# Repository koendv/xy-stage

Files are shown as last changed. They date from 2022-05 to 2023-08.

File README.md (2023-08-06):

# Microscope XY Stage

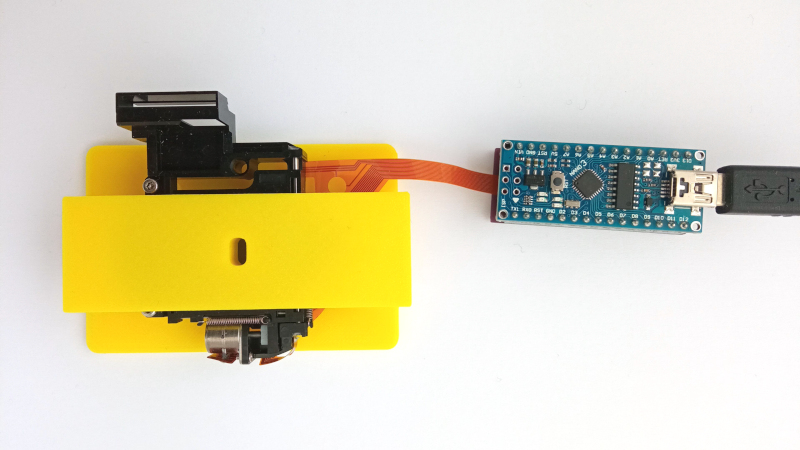
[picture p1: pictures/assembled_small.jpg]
assembled


This is a small computer-controlled mechanical microscope stage, with a movement of 2.4mm in both x and y, with a resolution of 5 &micro;m. Design goal is low component cost.

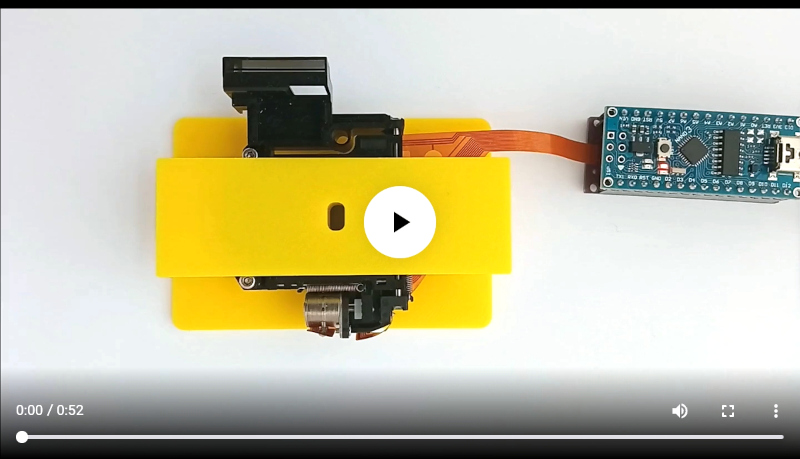
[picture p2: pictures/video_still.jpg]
video (https://vimeo.com/698148429)


[video](pictures/xy_stage.mp4) of the stage in motion.

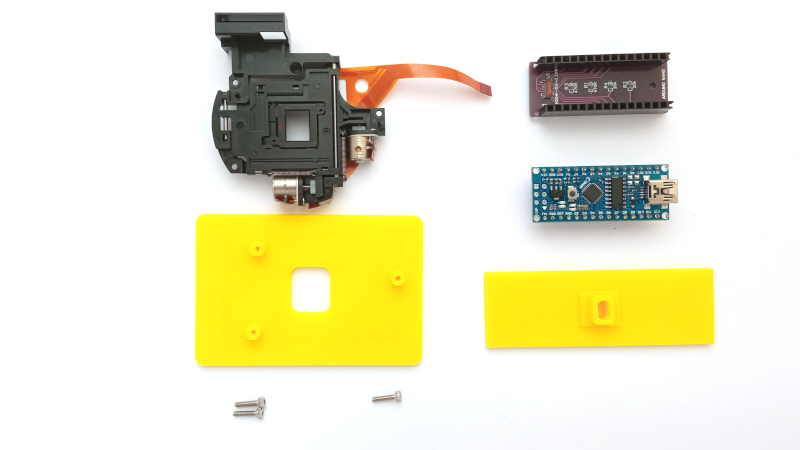
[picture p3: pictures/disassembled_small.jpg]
disassembled


The stage consists of

- mechanical part
- adapter plates
- connector board
- arduino nano controller
- firmware

## mechanical part

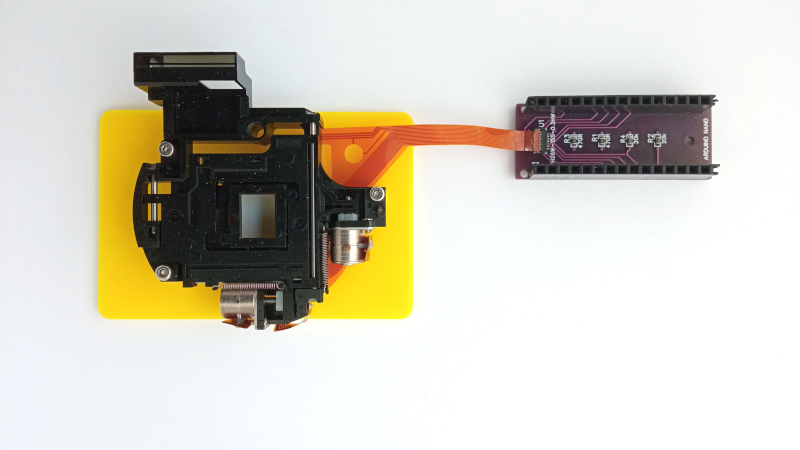
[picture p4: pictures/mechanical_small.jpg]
mechanical


Picture of mechanical part (to the left) and connector board (to the right).
The mechanical part is the [motion compensation part of a digital camera](https://www.aliexpress.com/item/32972295033.html), bought from aliexpress. All signals are on a flat flexible cable.

The mechanical part consists of a small carriage, two stepper motors and two slotted optocouplers, one for x and one for y. The stepper motors have a step size of  10 &micro;m. The stepper motors are run in half-stepping mode, resulting in a resolution of  5 &micro;m.

## adapter plates

The adapter plates give the microscope stage a flat base to sit on, and a flat top to put a microscope slide on.

The [adapter plates](openscad/) are designed in openscad and 3D printed. The size of the carriage is 25mmx75mm, the same as a standard microscope slide. I've snipped a few plastic pieces off from the movement to make everything fit. Holes can be threaded with hand tapping tools, or reamed with a small drill.

## connector board

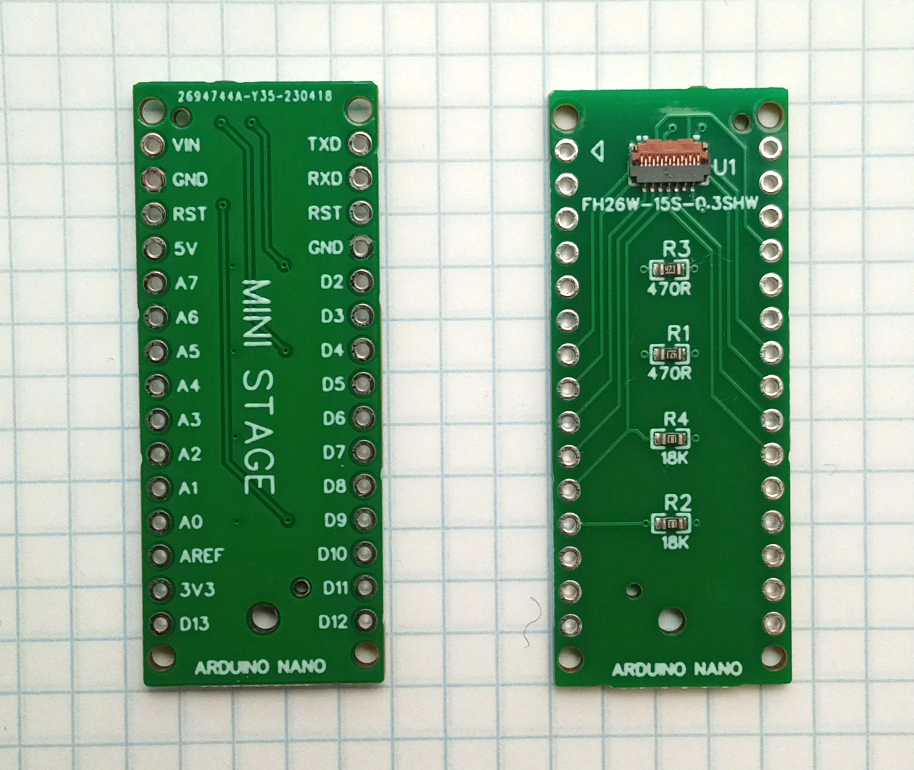
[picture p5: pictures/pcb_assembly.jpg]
pcb connector board


The [connector board](easyeda/Schematic_xy%20stage%20breakout_2023-05-13.pdf) breaks out the flat cable to the arduino pins. The xy stage contains two optical endstops, one for x and one for y. This is the [schematic](pictures/xystage_endstop.pdf) of one such optical endstop. There are current-limiting resistors for the optocoupler led, and pull-down resistors for the optocoupler output.  The stepper motors are so small you can connect them directly to the microcontroller pins.

The flat cable connector has a small tab. Lift the tab to insert or remove the flat cable. Push the tab down to fix the flat cable in place.

The [board project is at easyeda](https://oshwlab.com/koendv/xy-stage-breakout); and I've put up [gerbers at github](easyeda/).

The easiest way to obtain a pcb board is to have it assembled for you. All files needed for pcb assembly are in the [easyeda](easyeda/) directory:

- Gerber files
- Bill of Materials ("BOM")
- Pick and Place file ("CPL")

The Gerber files order the printed circuit board. The Bill of Materials orders the components. The Pick and Place file orders the components to be soldered to the board.

This is a walk-through of the ordering process:

- Log in to [jlcpcb.com](https://jlcpcb.com/).
- Click "Order now"
- Click "Add gerber file"
- Select file "Gerber_PCB_xy stage breakout_2023-05-13.zip"
- Select "PCB Assemly"
- Choose "Assemble top side"
- Click "Confirm"
- Click "Next"
- Click "Add BOM File"
- Select file "BOM_PCB_xy stage breakout_2023-05-13.csv"
- Click "Add CPL File"
- Select file "PickAndPlace_PCB_xy stage breakout_2023-05-13.csv"
- Click "Process BOM and CPL"
- Next to the flat cable connector it says "No part selected". Click "Search". After the part has been found, click "Select".
- Click "Next"
- In product description, choose "Research/Education/DIY/Entertainment", "DIY"
- Click "Save to cart"
- Check out order

Make sure all parts are available before ordering assembly.

## arduino nano controller

The microcontroller is a 5V 16MHz arduino nano. This processor was chosen because it can drive the stepper motor pins directly, at low cost. The arduino nano plugs in in the connector board.

Two firmware are available for the xy stage: an arduino sketch and the grbl g-code motion controller.

## arduino sketch

The [arduino/ directory](arduino/) contains an arduino project for the xy stage.
To install this firmware in the arduino nano, start up the arduino IDE. Open the file [xystage.ino](arduino/xystage/xystage.ino) in the arduino IDE,
In the arduino IDE, choose "Tools -> Board -> Arduino AVR Boards -> Arduino Nano", compile and upload.

Connect to the arduino serial port with a terminal emulator, and get this prompt:

```
xy stage - w forward s backward a left d right x home
ok
```

Move the stage using the WASD keys: w is forward, s is backward, a is left, d is right. x homes the stage, and if you press shift the stage moves ten times faster.

| key | action |
|---|---|
| w | forward 1 step |
| s | backward 1 step |
| a | left 1 step |
| d | right 1 step |
| W | forward 10 steps |
| S | backward 10 steps |
| A | left 10 steps |
| D | right 10 steps |
| x | home |

If after power-up the led blinks and the serial console prints  ``error`` then homing failed. Check the flat flexible cable connections, and that the carriage can move freely.

## grbl

grbl logo (https://github.com/gnea/grbl/wiki)

[grbl](https://github.com/gnea/grbl/wiki) is a g-code motion controller for the arduino nano. grbl allows stage control using G-code commands.

Example: Set the feed rate. Starting at the origin, first move the stage 1 mm in x, then 1 mm in y.

```
> Grbl 1.1h ['$' for help]
< F100
> ok
< G1X1
> ok
< G1Y1
> ok
```

See the [grbl/ directory](grbl/) for grbl firmware for the arduino nano.

Using G-code is interesting if you wish to automate a microscope.

## micro-manager

[micro-manager](https://micro-manager.org/) is open source software for control and automation of microscope hardware. See the [micro-manager/ directory](micro-manager/) for using the xy-stage with micro-manager.

## closing thoughts

Looking back, the adapter plates could easily be improved. The adapter plates were printed in yellow, on a Prusa FDM printer. If I had to do this again, I would 3D print the adapter plates in a matte dark grey or black, not yellow. Using SLS or MJF, not FDM, to be able to design a carriage that weighs less yet is more rigid. And probably ordered at [jlcpcb](https://3d.jlcpcb.com/), the same place I had the printed circuits made.

## bill of Materials

The list of materials used to build this project:

|Name|Part|Qty|
|---|---|---|
|R1, R3|470R 0603|2|
|R2, R4|18K 0603|2|
|U1|Hirose FH26W-15S-0.3SHW(60)|1|
||20pin 2.54mm single row female header|2|
||arduino nano 3.0 atmega328|1|
||[small xy stage](https://www.aliexpress.com/item/32972295033.html)|1|
||M2x8 screw|3|
||pcb|1|
||3D printed parts|1|

ko-fi (https://ko-fi.com/Q5Q03LPDQ)

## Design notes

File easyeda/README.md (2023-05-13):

These are the design files for the connector board.
The connector board is a [project at easyeda](https://oshwlab.com/koendv/xy-stage-breakout).

- [Schematic](Schematic_xy stage breakout_2023-05-13.pdf)
- [PCB](PCB_PCB_xy stage breakout_2023-05-13.pdf)
- [Gerbers](Gerber_PCB_xy stage breakout_2023-05-13.zip).
- [Bill of Materials](BOM_PCB_xy stage breakout_2023-05-13.csv)
- [Pick and Place file](PickAndPlace_PCB_xy stage breakout_2023-05-13.csv)

The Gerbers order the printed circuit board; the Bill of Materials orders the components, and the Pick and Place file orders the components to be soldered to the printed circuit board.

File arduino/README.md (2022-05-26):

## Arduino project
This is the arduino project for the xy stage. Open the file "xystage.ino" in the Arduino IDE,
In the arduino IDE, choose "Tools -> Board -> Arduino AVR Boards -> Arduino Nano", compile and upload.

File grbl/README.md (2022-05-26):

# grbl for h-bridge

grbl is controller software that allows stage control using G-code commands.

This directory contains a patch to use the [grbl](https://github.com/gnea/grbl) G-code controller with the xy microscope stage.  This patch is needed because

- the steppers are connected to the controller pins as h-bridge, while grbl expects step/direction stepper drivers.
- the xy stage has homing switches at the center of the stage, while grbl prefers limit switches at the end of the stage.

## compilation

The flash upload command may differ for your setup. For compilation on linux, install arduino ide and set the path to use avr-gcc and avrdude from arduino:

```
export PATH=~/.arduino15/packages/arduino/tools/avr-gcc/7.3.0-atmel3.6.1-arduino7/bin/:~/.arduino15/packages/arduino/tools/avrdude/6.3.0-arduino17/bin/:$PATH
git clone https://github.com/koendv/xy-stage
git clone https://github.com/gnea/grbl
cd grbl/
patch -p1 < ../xy-stage/grbl/grbl_1_1h.patch
make
make flash
```

For compiling on Windows using the Arduino IDE, see [compiling GRBL](https://github.com/gnea/grbl/wiki/Compiling-Grbl)

## links

- [GRBL-H-Bridge](https://github.com/rakshithbk/GRBL-H-Bridge)
- [h-grbl](http://xn--zabaaganionemiejsce-8fd.pl/arduino/h-grbl/)

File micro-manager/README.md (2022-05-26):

# micro-manager

[micro-manager](https://micro-manager.org/) is open source software for control and automation of microscope hardware. This is a micro-manager driver for a mechanical stage that uses a grbl controller.

Instead of writing a separate driver for grbl, this patches the existing micro-manager RAMPS driver to use grbl g-code.

## compile

Patch micro-manager sources with _micro-manager-grbl.patch_:
```
 $ git clone --recursive https://github.com/micro-manager/micro-manager/
 $ cd micro-manager/mmCoreAndDevices/
 $ wget https://raw.githubusercontent.com/koendv/xy-stage/main/micro-manager/micro-manager-grbl.patch
 $ patch -p1 < micro-manager-grbl.patch
patching file DeviceAdapters/CNCMicroscope/RAMPSStage/RAMPS.cpp
patching file DeviceAdapters/CNCMicroscope/RAMPSStage/RAMPS.h
```

[Compile and install](https://github.com/micro-manager/micro-manager/blob/main/doc/how-to-build.md).

## configure

To configure, choose Devices -> Hardware Configuration Wizard.

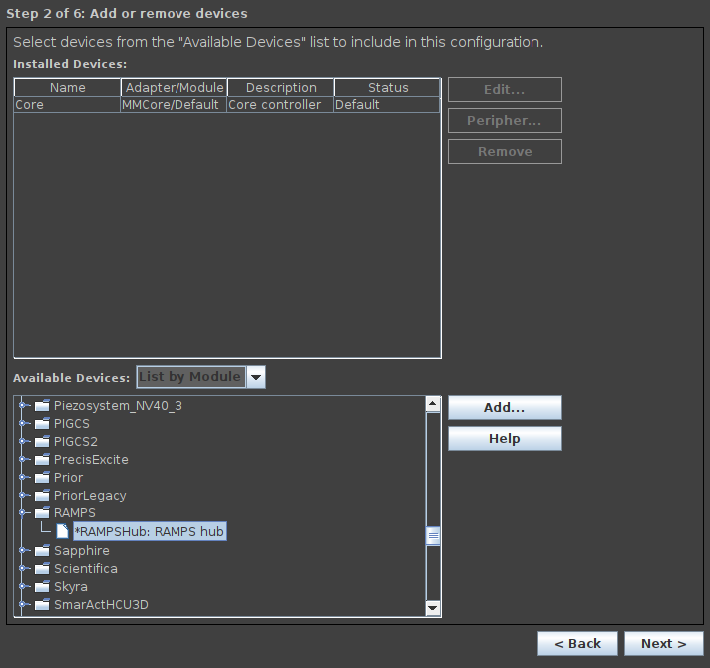
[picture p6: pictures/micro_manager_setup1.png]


Select xy stage serial port.

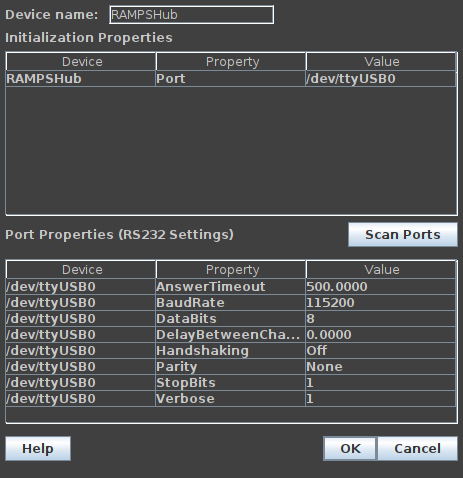
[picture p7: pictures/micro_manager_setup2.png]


Select only xy stage, not z stage.

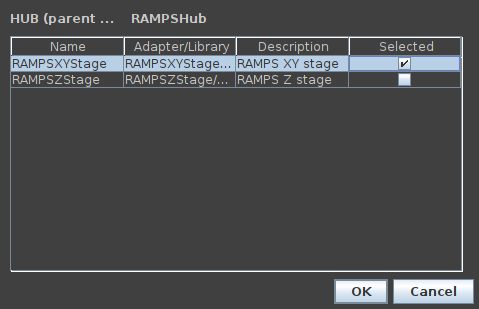
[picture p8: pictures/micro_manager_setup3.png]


Choose Devices -> Device Property Browser to set xy stage speed and acceleration. The values for RAMPSHub-Acceleration are written to grbl registers 120, 121 and 122. The values for RAMPSHub-Velocity are written to grbl registers 110, 111 and 112.

not truncated

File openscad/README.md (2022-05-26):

## openscad

disassembled.jpg

These are the design files for the adapter plates. The adapter plates are designed using [openscad](http://openscad.org). There are two versions of the carriage, one with a hole for illumination from below and one without.

- [source file](stage.scad)
- [stage top, solid](stage1.stl)
- [stage top, with hole for illumination](stage2.stl)
- [stage bottom](stageplate.stl)
- [stage bottom, with bracket to attach arduino nano](stageplate_arduinonano.stl)
- [stage floorplan](stage.svg)

Two 3D printing methods have been used:

- FDM, PETG material, [Prusa i3](https://www.treatstock.com/c/seaside-3d).
- SLA, LEDO 6060 resin, [jlcpcb 3d](https://jlcpcb.com/3d-printing)

In the end, how to print depends upon price.

Some ideas for improvements:

- more stable carriage, larger hole for through illumination if the other side of the xy table is up
- smaller and lighter carriage if 18x18x1mm cover slips are used instead of 75x25mm slides.
- arduino nano holder

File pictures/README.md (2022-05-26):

# pictures

|sliding table|
|---|
|assembled.jpg|
|mechanical.jpg|
|disassembled.jpg|
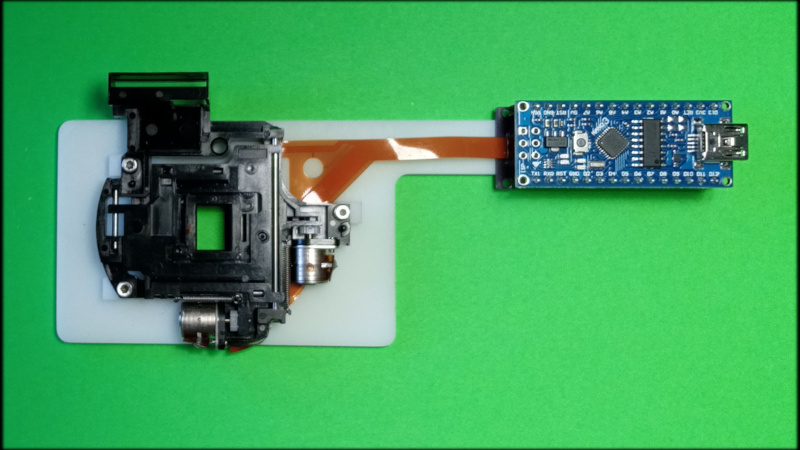
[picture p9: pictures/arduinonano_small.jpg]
arduinonano.jpg
||
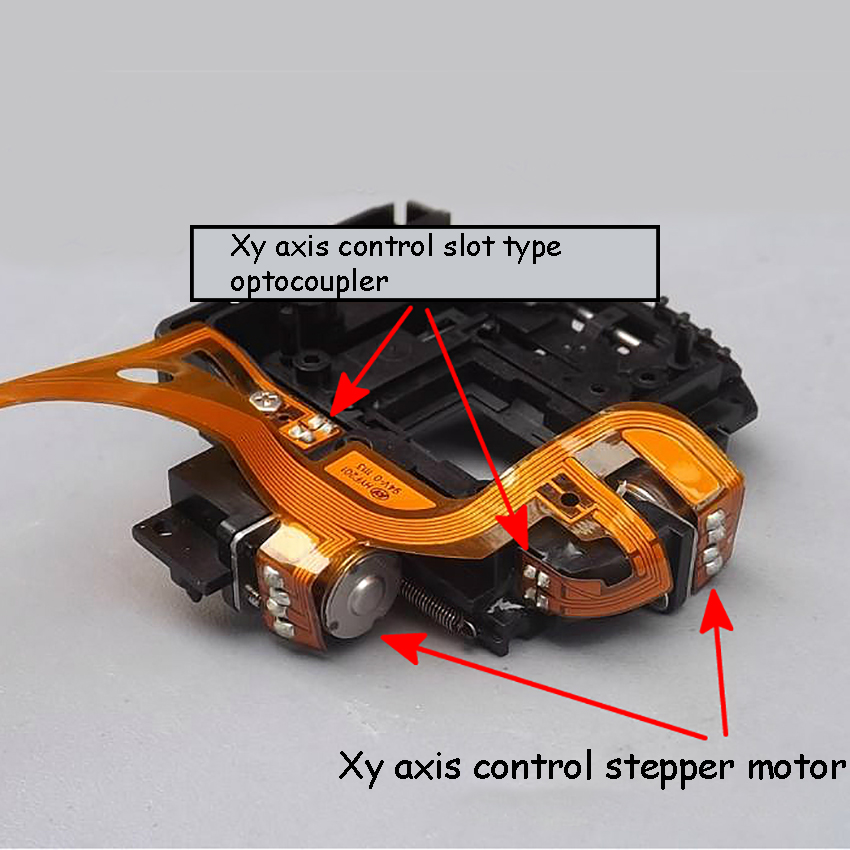
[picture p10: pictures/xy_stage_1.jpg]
xy_stage_1.jpg
||
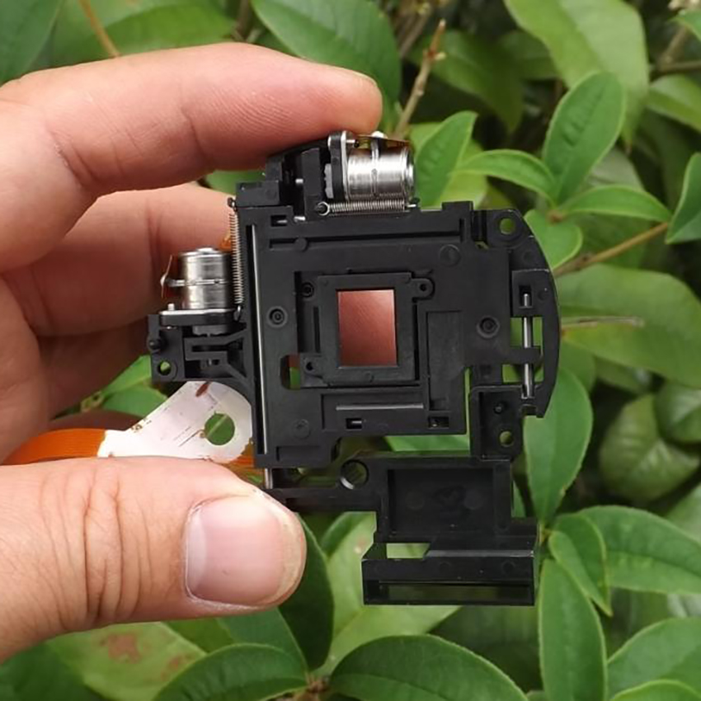
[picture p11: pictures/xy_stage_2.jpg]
xy_stage_2.jpg
||
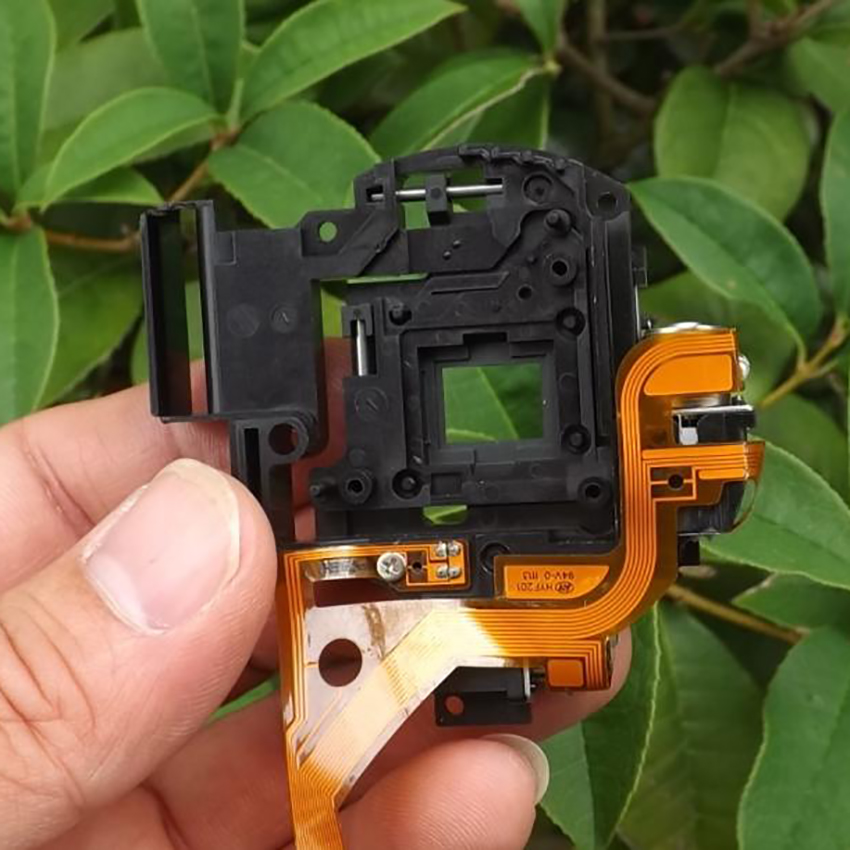
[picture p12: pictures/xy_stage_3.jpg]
xy_stage_3.jpg
||
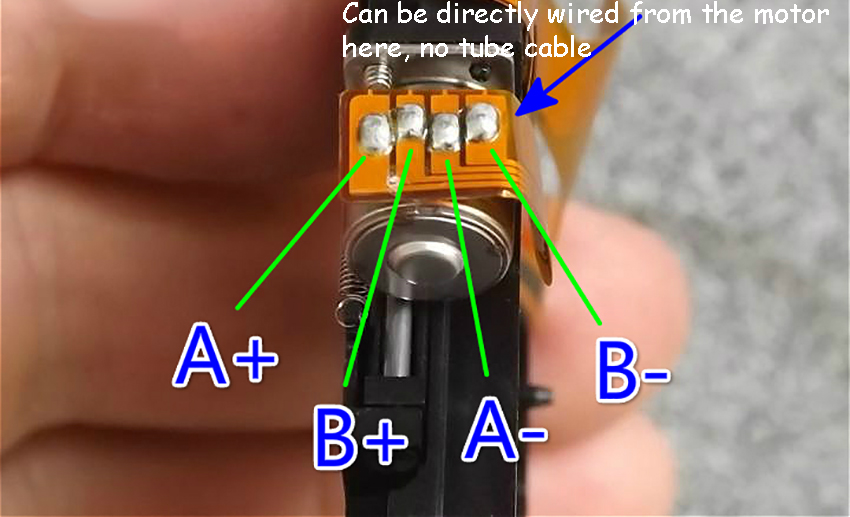
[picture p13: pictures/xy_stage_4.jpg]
xy_stage_4.jpg
||
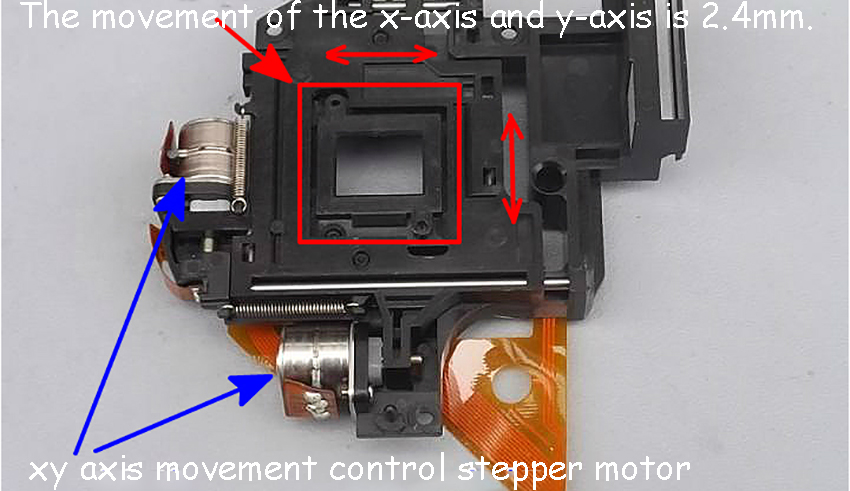
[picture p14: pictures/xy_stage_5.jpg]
xy_stage_5.jpg
||
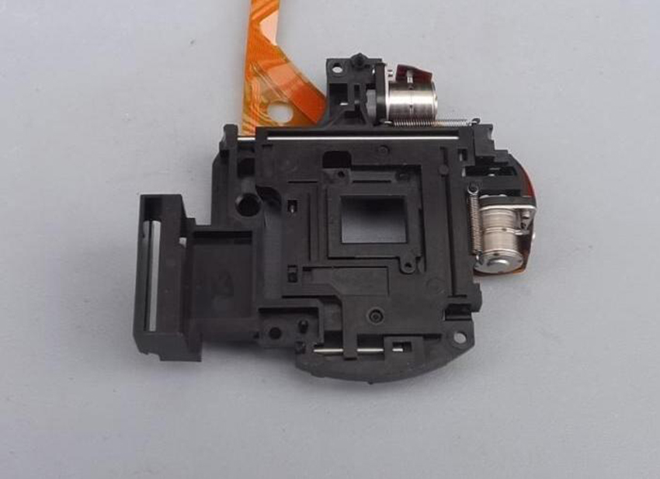
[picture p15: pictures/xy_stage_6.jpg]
xy_stage_6.jpg
||
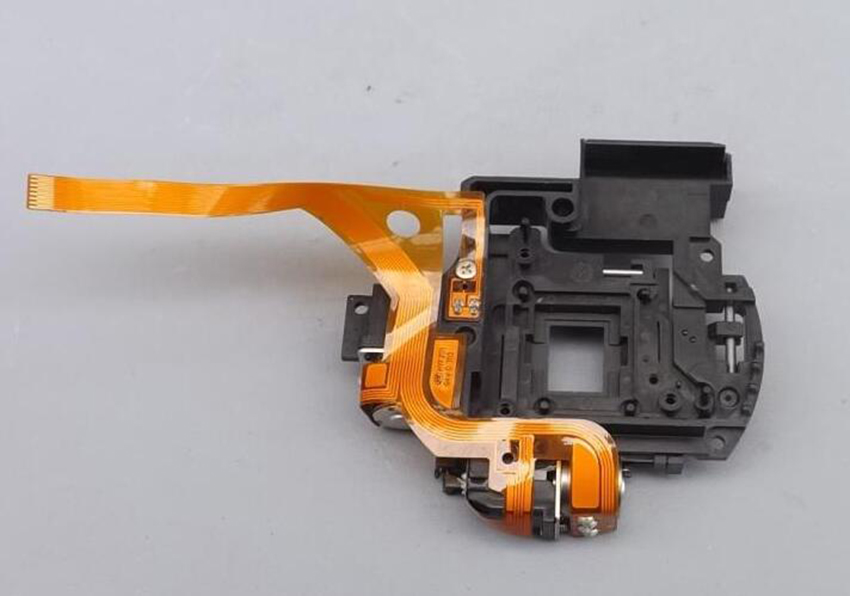
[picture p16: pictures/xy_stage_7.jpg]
xy_stage_7.jpg
||
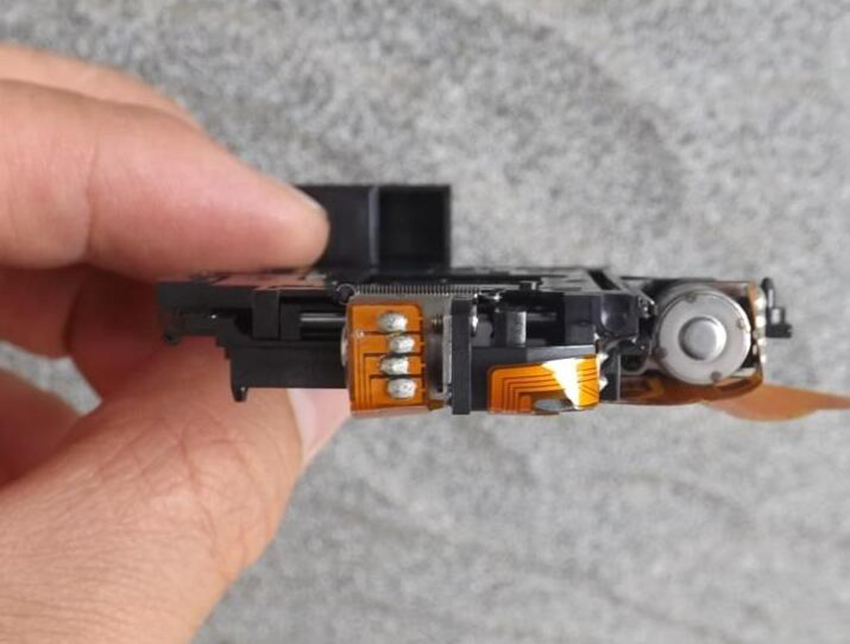
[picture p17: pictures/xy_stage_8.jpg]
xy_stage_8.jpg
||

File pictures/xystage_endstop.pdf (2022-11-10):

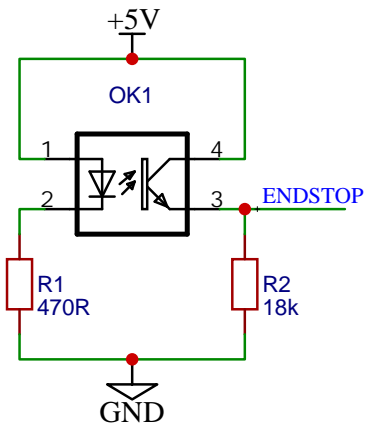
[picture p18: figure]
GND; ENDSTOP

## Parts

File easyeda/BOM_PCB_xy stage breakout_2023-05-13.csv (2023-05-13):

ID | Name | Designator | Footprint | Quantity | Manufacturer Part | Manufacturer | Supplier | Supplier Part | Price
1 | FH26W-15S-0.3SHW | U1 | FH26W-15S-0.3HW | 1 | FH26W-15S-0.3HW | Hirose | LCSC | C2840191
2 | 470R | R1,R3 | R0603 | 2 | 0603WAF4700T5E | UniOhm | LCSC | C23179 | 0.001
3 | 18K | R2,R4 | R0603 | 2 | 0603WAF1802T5E | UniOhm | LCSC | C25810 | 0.001
4 | HDR-F-2.54_1x15 | H1,H2 | HDR-F-2.54_1X15 | 2 |  |  | LCSC | C124408 | 0.204

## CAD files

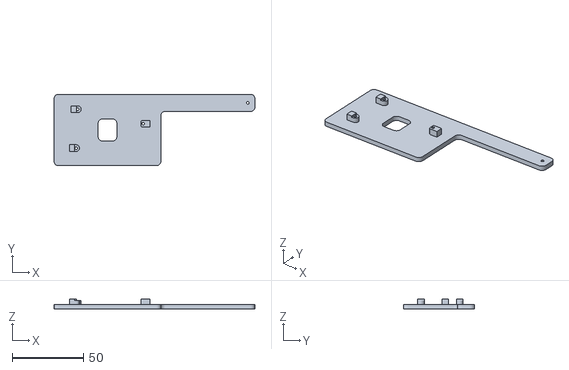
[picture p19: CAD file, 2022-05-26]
openscad/stageplate_arduinonano.stl
141.0 x 50.0 x 7.00

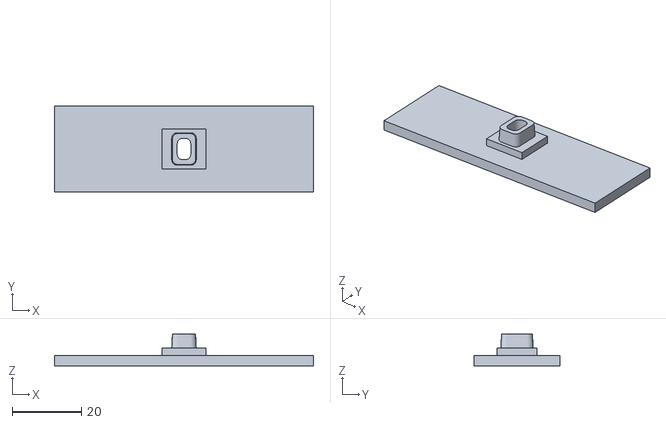
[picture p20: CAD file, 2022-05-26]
openscad/stage2.stl
75.0 x 25.0 x 9.20

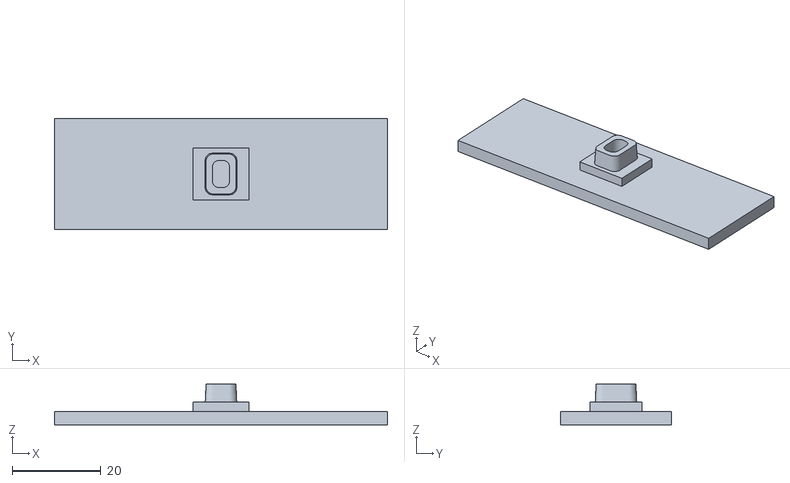
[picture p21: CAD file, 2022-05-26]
openscad/stage1.stl
75.0 x 25.0 x 9.20

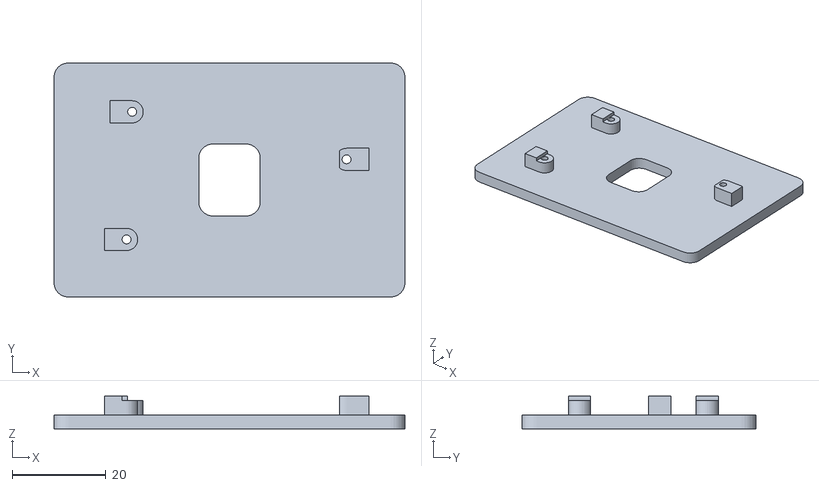
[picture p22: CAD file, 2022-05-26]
openscad/stageplate.stl
75.0 x 50.0 x 7.00

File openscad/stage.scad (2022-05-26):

$fn = $preview?16:32;
eps1 = 0.001;
eps2 = 2*eps1;
nozzle = 0.4;

plate_x = 75.0;
plate_y = 50.0;

// pillars for screws
d1 = 1.9;  // inner diameter pillar
d2 = 4.75; // outer diameter pillar
// screws
dscrew = 25.4;
alpha1 = 90+120;
alpha2 = 90+55;
alpha3 = 90-80;
// screw 1
x1 = dscrew * cos(alpha1);
y1 = dscrew * sin(alpha1);
t1 = (d2-d1)/2; // bump on pillar
cut1 = 0.9;     // bump on pillar
// screw 2
x2 = dscrew * cos(alpha2);
y2 = dscrew * sin(alpha2);
t2 = (d2-d1)/2; // bump on pillar
cut2 = 0.9;     // bump on pillar
// screw 3
x3 = dscrew * cos(alpha3);
y3 = dscrew * sin(alpha3);
t3 = -d2+0.9;   // cut on pillar
cut3 = 4.0;     // cut on pillar

// central hole size
l1 = 7.12;
l2 = 9.37;

h1 = 3.0;
h2 = 4.0;

dmax = 3.0;

// support for attaching arduino nano
pcb_support = true;

pcb_x = 66.0;
pcb_y = 12.0;
pcbscrew_x = pcb_x - 5.0;
pcbscrew_d = 2.0;

module stageplate() {
    difference() {
        stageplate_body();
        stageplate_holes();
    }
}

module stageplate_body() {
    translate([-plate_x/2, -plate_y/2, 0])
    linear_extrude(h1)
    offset(-dmax)
    offset(2*dmax)
    offset(-dmax)
    union() {
        square([plate_x, plate_y]);
        if (pcb_support)
        translate([plate_x, plate_y-pcb_y, 0])
        square([pcb_x, pcb_y]);
    }

    // screws
    translate([x1, y1, h1-eps1])
    difference() {
        union() {
            cylinder(h=h2, d=d2);
            translate([-d2, -d2/2, 0])
            cube([d2, d2, h2]);
        }
        translate([t1-d2/2, -d2, h2-cut1])
        cube([d2, 2*d2, h2]);
    }
    translate([x2, y2, h1-eps1])
    difference() {
        union() {
            cylinder(h=h2, d=d2);
            translate([-d2, -d2/2, 0])
            cube([d2, d2, h2]);
        }
        translate([t2-d2/2, -d2, h2-cut2])
        cube([d2, 2*d2, h2]);
    }
    translate([x3, y3, h1-eps1])
    difference() {
        union() {
            cylinder(h=h2, d=d2);
            translate([0, -d2/2, 0])
            cube([d2, d2, h2]);
        }
        translate([t3-d2/2, -d2/2, h2-cut3])
        cube([d2, d2, h2+eps1]);
    }
}

module stageplate_holes() {
    h = h1+h2+eps2;
    translate([x1, y1, -eps1])
    cylinder(h=h, d=d1);
    translate([x2, y2, -eps1])
    cylinder(h=h, d=d1);
    translate([x3, y3, -eps1])
    cylinder(h=h, d=d1);
    translate([-l1/2, -l2/2, -eps1])
    linear_extrude(h)
    offset(dmax)
    square([l1, l2]);
    // pcb
    if (pcb_support)
    translate([plate_x/2 + pcbscrew_x, plate_y/2-pcb_y/2, -eps1])
    cylinder(h=h, d=d1);
}


stage_x = 75.0;
stage_y = 25.0;
stage_z = 3.0;
foot_x = 13.0 - nozzle;
foot_y = 12.0 - nozzle;
foot_z = 2.2;
chamfer = 1.6;
wall_thickness = 1.6;
module stage(no_hole) {
    difference() {
        stage_body();
        stage_holes(no_hole); // no_hole = true or false
    }
}

module stage_body() {
    translate([-stage_x/2, -stage_y/2, 0])
    cube([stage_x, stage_y, stage_z]);
    translate([-foot_x/2, -foot_y/2, stage_z-eps1])
    cube([foot_x, foot_y, foot_z]);

    hull() {
        translate([0, 0, h1+foot_z+4])
        linear_extrude(eps1)
        offset(chamfer)
        offset(-chamfer)
        square([l1-nozzle, l2-nozzle], center = true);
        translate([0, 0, h1+foot_z])
        linear_extrude(eps1)
        offset(chamfer)
        offset(-chamfer)
        square([l1, l2], center = true);
    }
}

module stage_holes(solid = true) {
    translate([0, 0, solid ? -h1-foot_z-eps1 : 0])
    translate([-l1/2, -l2/2, h1+foot_z-eps1])
    linear_extrude(h1*10)
    offset(wall_thickness)
    offset(-2*wall_thickness)
    square([l1, l2]);
}

module assembly() {
    stageplate();
    translate([0, 0, 10])
    mirror([0,0,1])
    stage(false); // no hole in stage
}

assembly();
//projection()
//stageplate();
//stage(false); // no hole in stage
//stage(true); // hole in stage

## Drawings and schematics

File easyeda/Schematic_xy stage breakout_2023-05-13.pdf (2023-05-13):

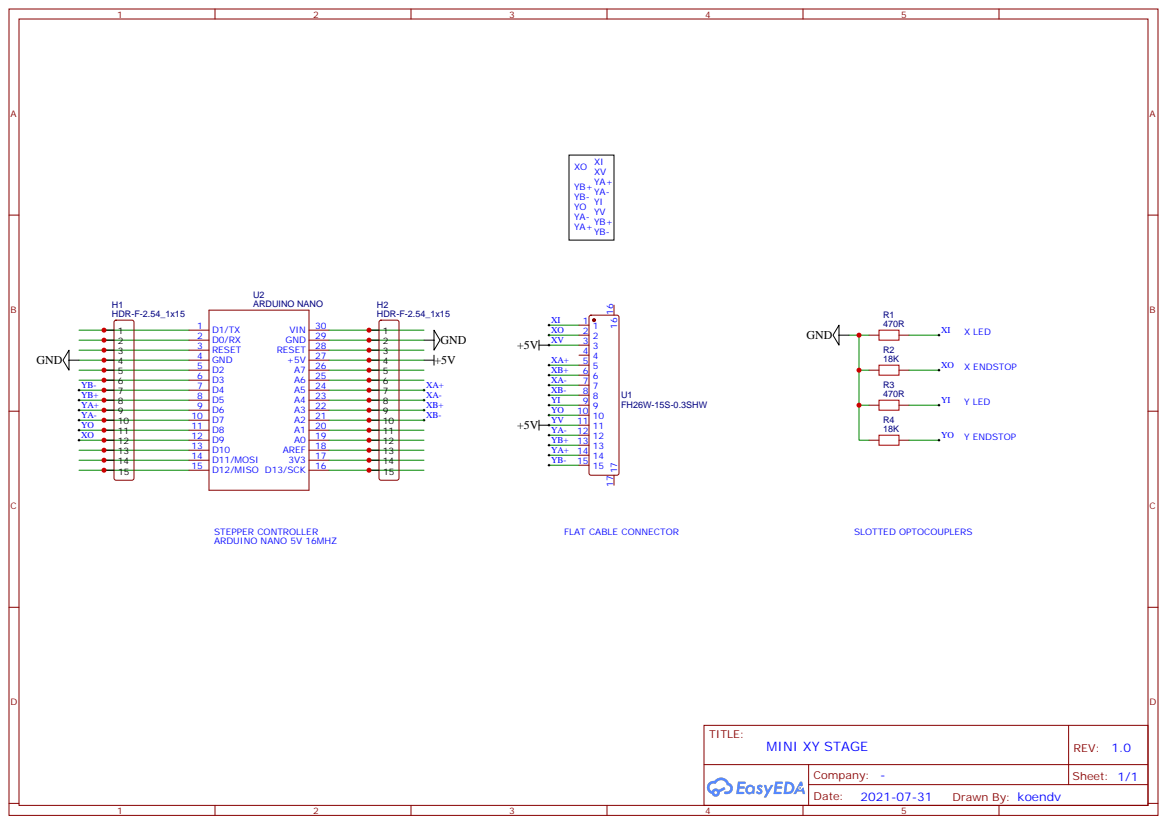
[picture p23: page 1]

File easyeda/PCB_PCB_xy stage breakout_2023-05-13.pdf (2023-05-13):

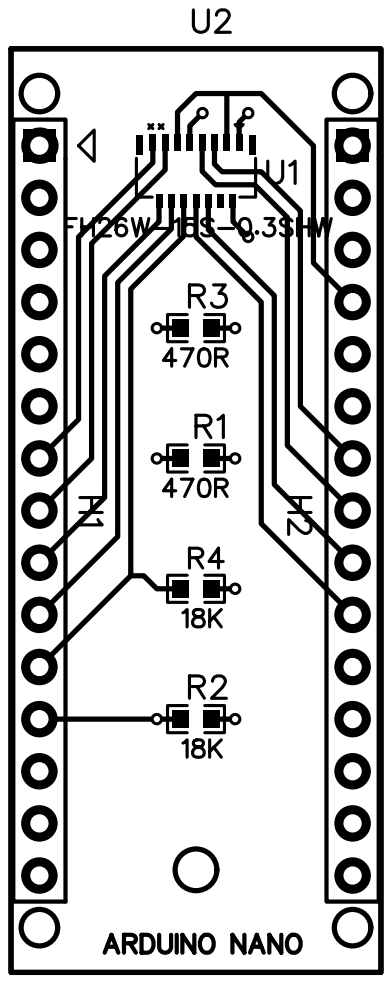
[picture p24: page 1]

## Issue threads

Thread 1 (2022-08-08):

### ISSUE TITLE
Connector board

### ISSUE THREAD

**Issue by gtnz** [koendv/xy-stage#1]
Hello. 
Sorry, I don’t know where on github they ask questions, so I open issue.

Where can I get a connector board like in your project?

**Comment by koendv** [comment]
Thank you for your interest. This is a good question.

The board I use I soldered myself, by hand. If you wish to, I can send it to you for 15 EUR + what the post office charges me to send a small packet.

Soldering by hand becomes unpractical, even for small numbers. There are companies like jlcpcb, seeedstudio, elecrow that do pcb assembly for you, but then you have not one board, but 5.

**Comment by koendv** [comment]
I added documentation how I ordered the pcb and components, see https://github.com/koendv/xy-stage#connector-board
HTH

**Comment by gtnz** [comment]
Thank you very much

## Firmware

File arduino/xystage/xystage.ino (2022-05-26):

/* 
 * microscope mechanical stage
 * commands:
 * w forward s backward a left d right q home
 * W fast forward S fast backward A fast left D fast right
 */

#include <Arduino.h>

// B (pin D8, D9: endstops)
// C (pin A2..A5: x stepper)
// D (pin D4..D7: y stepper)

// stop homing if homing switch does not change after HOME_MAX_STEPS steps
#define HOME_MAX_STEPS 720

#define X0_MAX 240
#define X0_MIN -240
#define Y0_MAX 240
#define Y0_MIN -240

#define ENDSTOP_X 8
#define ENDSTOP_Y 9

#define STEPPER_X_A1 (0x01 << PINC5)
#define STEPPER_X_A2 (0x01 << PINC4)
#define STEPPER_X_B1 (0x01 << PINC3)
#define STEPPER_X_B2 (0x01 << PINC2)

#define STEPPER_Y_A1 (0x01 << PIND4)
#define STEPPER_Y_A2 (0x01 << PIND5)
#define STEPPER_Y_B1 (0x01 << PIND6)
#define STEPPER_Y_B2 (0x01 << PIND7)

#define STEPPER_PORT_X PORTC
#define STEPPER_PORT_Y PORTD

#define STEPPER_DDR_X DDRC
#define STEPPER_DDR_Y DDRD

#define ALL_STEPPER_PINS_X (STEPPER_X_A1 | STEPPER_X_A2 | STEPPER_X_B1 | STEPPER_X_B2)
#define ALL_STEPPER_PINS_Y (STEPPER_Y_A1 | STEPPER_Y_A2 | STEPPER_Y_B1 | STEPPER_Y_B2)

const int stepper_table_x[8]{ STEPPER_X_A1, STEPPER_X_A1 | STEPPER_X_B1, STEPPER_X_B1, STEPPER_X_B1 | STEPPER_X_A2, STEPPER_X_A2, STEPPER_X_A2 | STEPPER_X_B2, STEPPER_X_B2, STEPPER_X_B2 | STEPPER_X_A1 };
const int stepper_table_y[8]{ STEPPER_Y_A1, STEPPER_Y_A1 | STEPPER_Y_B1, STEPPER_Y_B1, STEPPER_Y_B1 | STEPPER_Y_A2, STEPPER_Y_A2, STEPPER_Y_A2 | STEPPER_Y_B2, STEPPER_Y_B2, STEPPER_Y_B2 | STEPPER_Y_A1 };

static unsigned int step_x = 0;
static unsigned int step_y = 0;

static int x0 = 0;
static int y0 = 0;

bool homed = false;
uint32_t last_update_millis = 0;

void update_pins() {
  step_x %= 8;
  step_y %= 8;
  STEPPER_PORT_X = (STEPPER_PORT_X & ~ALL_STEPPER_PINS_X) | stepper_table_x[step_x];
  STEPPER_PORT_Y = (STEPPER_PORT_Y & ~ALL_STEPPER_PINS_Y) | stepper_table_y[step_y];
  delay(5);  // lower for faster
  last_update_millis = millis();
}

void idle_pins() {
  uint32_t now_millis = millis();
  if (now_millis > last_update_millis + 30000) {
    // sleep
    STEPPER_PORT_X = (STEPPER_PORT_X & ~ALL_STEPPER_PINS_X);
    STEPPER_PORT_Y = (STEPPER_PORT_Y & ~ALL_STEPPER_PINS_Y);
    last_update_millis = millis();
  }
}
void home() {
  int maxcnt;
  homed = false;
  maxcnt = HOME_MAX_STEPS;
  /* x axis  home */
  while (digitalRead(ENDSTOP_X)) {
    if (--maxcnt == 0) return;
    step_x += 7;
    update_pins();
  };
  while (!digitalRead(ENDSTOP_X)) {
    if (--maxcnt == 0) return;
    step_x += 1;
    update_pins();
  };
  /* y axis  home */
  maxcnt = HOME_MAX_STEPS;
  while (digitalRead(ENDSTOP_Y)) {
    if (--maxcnt == 0) return;
    step_y += 7;
    update_pins();
  };
  while (!digitalRead(ENDSTOP_Y)) {
    if (--maxcnt == 0) return;
    step_y += 1;
    update_pins();
  };
  x0 = 0;
  y0 = 0;
  homed = true;
}

// print coordinates in micron
void print_coords() {
  Serial.print(x0 * 5);
  Serial.print(' ');
  Serial.print(y0 * 5);
  Serial.println();
}

void stage_left() {
  if (x0 > X0_MIN) {
    step_x += 7;
    --x0;
    update_pins();
  }
}

void stage_right() {
  if (x0 < X0_MAX) {
    step_x += 1;
    x0++;
    update_pins();
  }
}

void stage_forward() {
  if (y0 > Y0_MIN) {
    step_y += 7;
    --y0;
    update_pins();
  }
}

void stage_backward() {
  if (y0 < Y0_MAX) {
    step_y += 1;
    y0++;
    update_pins();
  }
}

// blink led once per second if homing failed
  void blink_led() {
  static uint8_t led_val = 0xff;
  uint8_t new_val = !homed && ((millis() >> 9) & 0x1);
  if (led_val != new_val) {
    digitalWrite(LED_BUILTIN, new_val);
    led_val = new_val;
  }
}

void setup() {
  Serial.begin(115200);
  pinMode(ENDSTOP_X, INPUT);
  pinMode(ENDSTOP_Y, INPUT);
  pinMode(LED_BUILTIN, OUTPUT);
  digitalWrite(LED_BUILTIN, 0);
  STEPPER_DDR_X |= ALL_STEPPER_PINS_X;
  STEPPER_DDR_Y |= ALL_STEPPER_PINS_Y;
  update_pins();
  Serial.println("xy stage - w forward s backward a left d right x home");
  home();
  Serial.println(homed ? "ok" : "error");
}

void loop() {
  const int repeat_cnt = 10;
  if (Serial.available() > 0) {
    char ch = Serial.read();
    // on qwerty keyboards use WASD keys; on azerty keyboard use ZQSD keys.
    switch (ch) {
      case 'a':
      case 'q':
        stage_left();
        break;
      case 'd':
        stage_right();
        break;
      case 'w':
      case 'z':
        stage_forward();
        break;
      case 's':
        stage_backward();
        break;
      case 'A':
      case 'Q':
        for (int i = 0; i < repeat_cnt; i++)
          stage_left();
        break;
      case 'D':
        for (int i = 0; i < repeat_cnt; i++)
          stage_right();
        break;
      case 'W':
      case 'Z':
        for (int i = 0; i < repeat_cnt; i++)
          stage_forward();
        break;
      case 'S':
        for (int i = 0; i < repeat_cnt; i++)
          stage_backward();
        break;
      case 'X':
      case 'x':
        home();
        break;
      default:
        break;
    }
    print_coords();
  }
  idle_pins();
  blink_led();
}
// not truncated

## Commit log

2022-07-30 pcb fab
2023-03-05 with wires
2023-05-13 pcb assembly
    [BOM_PCB_xy stage breakout_2022-04-08.csv, BOM_PCB_xy stage breakout_2023-05-13.csv, PickAndPlace_PCB_xy stage breakout_2022-04-08.csv, PickAndPlace_PCB_xy stag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]
